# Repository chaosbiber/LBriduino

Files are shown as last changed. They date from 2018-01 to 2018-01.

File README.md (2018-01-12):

# LBriduino
## Description
This is a PCB design for keencave's [LBridge](https://github.com/keencave/LBridge) code. It's my very first design and still in testing, dragons beware!

Made with free version of EAGLE for BM019 and RFDuino.

The switch has the states On (1-2) and Off/Testing (2-3). The battery can be charged in any state, in the off-state power for the NFC and RFDuino modules is disconnected. But there are two testing vias that can be shorted or connected to an ampere meter.

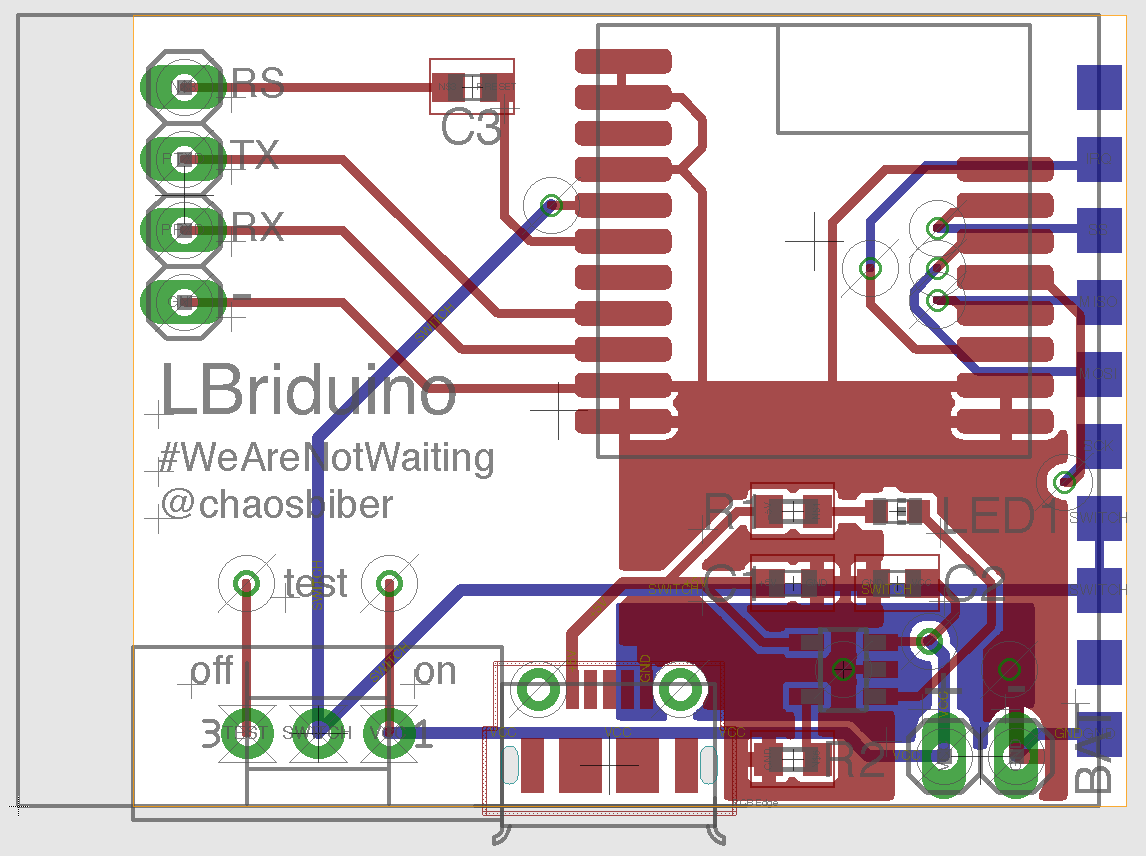
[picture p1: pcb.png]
PCB screenshot


## Parts
(product links from 2017/12/10)

* BM019  
http://www.solutions-cubed.com/bm019/  
http://www.warburtech.co.uk/products/modules/solutions.cubed.bm019.serial.to.nfc.converter/
* RFduino RFD22301  
https://www.mouser.de/ProductDetail/RF-Digital-Wireless/RFD22301/
* Lipo Charger IC MCP73831T-2ACI/OT
* C1/C2: Capacitor 0603 4.7µF (measured 3.8µF)
* C3: Capacitor 0603 100nF (to program RFDuino, smaller capacity was recommended but 100nF works for me)
* R1: 330 Ohm
* R2: 3kOhm (for ~333mA charging speed, default 2kOhm for ~500mA. Ic = 1000/R2)
* red LED 0603
* Sliding switch SPDT (generic, I ordered Apem MHSS1105)
* Molex 105017-0001 USB micro-B connector
* USB programmer for the RFDuino (RFD22121), or any adapter with serial connection at 3.3V level

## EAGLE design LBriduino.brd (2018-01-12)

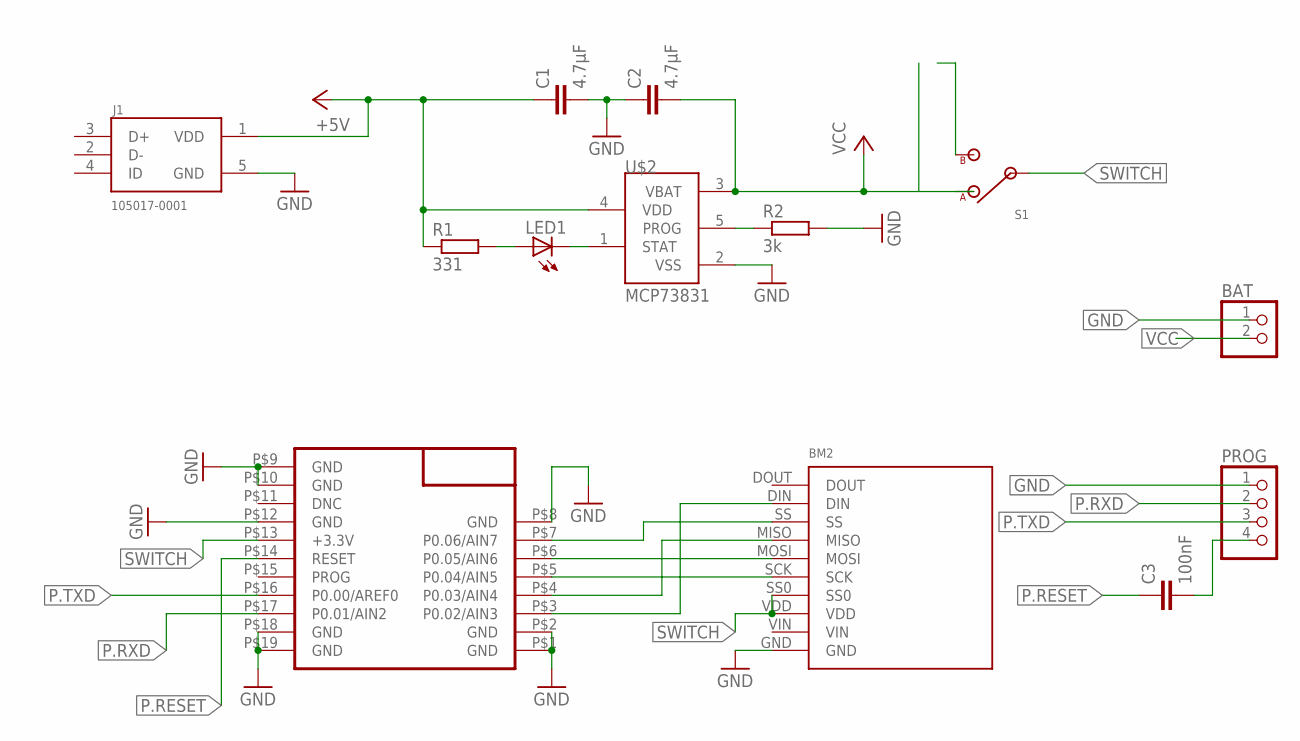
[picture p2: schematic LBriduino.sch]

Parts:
BAT: PINHD-1X2; 1X02
BM2: BM019
C1, C2: 4.7µF; C0603
C3: 100nF; C0603
J1: 105017-0001; MOLEX_105017-0001
LED1: LEDCHIP-LED0603; CHIP-LED0603
PROG: PINHD-1X4; 1X04
R1: 331; R0603
R2: 3k; R0603
S1: STS121PC04
U$1: RFD22301; RFD21733
U$2: MCP73831; SOT23-5L

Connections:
+5V: C1.1, J1.1 (VDD), R1.1, U$2.4 (VDD)
GND: BAT.1, BM2.GND, C1.2, C2.1, J1.5 (GND), PROG.1, R2.2, U$1.P$1 (GND), U$1.P$2 (GND), U$1.P$8 (GND), U$1.P$9 (GND), U$1.P$10 (GND), U$1.P$12 (GND), U$1.P$18 (GND), U$1.P$19 (GND), U$2.2 (VSS)
IRQ: BM2.DIN, U$1.P$3 (P0.02/AIN3)
MISO: BM2.MISO, U$1.P$4 (P0.03/AIN4)
MOSI: BM2.MOSI, U$1.P$6 (P0.05/AIN6)
unnamed: LED1.A, R1.2
unnamed: LED1.C, U$2.1 (STAT)
unnamed: C3.2, PROG.4
unnamed: R2.1, U$2.5 (PROG)
P.RESET: C3.1, U$1.P$14 (RESET)
P.RXD: PROG.2, U$1.P$17 (P0.01/AIN2)
P.TXD: PROG.3, U$1.P$16 (P0.00/AREF0)
SCK: BM2.SCK, U$1.P$5 (P0.04/AIN5)
SS: BM2.SS, U$1.P$7 (P0.06/AIN7)
SWITCH: BM2.SS0, BM2.VDD, S1.2, U$1.P$13 (+3.3V)
TEST: S1.3
VCC: BAT.2, C2.2, S1.1, U$2.3 (VBAT)

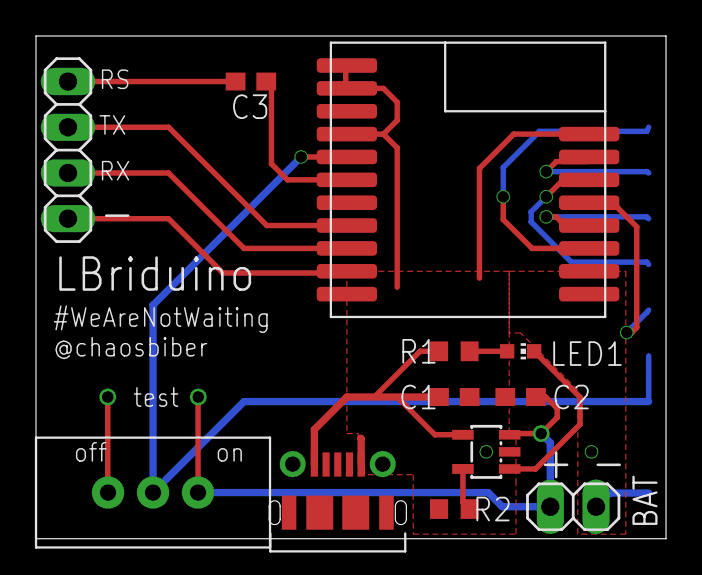
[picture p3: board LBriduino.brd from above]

Board: 2 copper layers, 35.0 x 27.9 mm, 13 parts (1 on the bottom side), 16 nets.

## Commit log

2017-12-11 added board files, README and screenshot
    [LBriduino.brd, LBriduino.sch]
2017-12-11 minor re-wireing, updated pic, specified usb connector in description
    [LBriduino.brd, LBriduino.sch]
2017-12-11 reduced groundplane, used traces instead
    [LBriduino.brd]
2017-12-11 changed BM019 voltage input from VIN to VDD, added testing points for ampere meter in off-mode
    [LBriduino.brd, LBriduino.sch]
2018-01-11 redesign: missing ground bugfix, charging-IC-cooling, bluetooth-area copper-free
    [LBriduino.brd, LBriduino.sch]
2018-01-12 made it smaller
    [LBriduino.brd, LBriduino.sch]
